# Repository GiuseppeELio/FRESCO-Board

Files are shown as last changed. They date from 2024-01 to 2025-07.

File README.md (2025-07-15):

#       PRC Measurement Station including TDrop and PCool
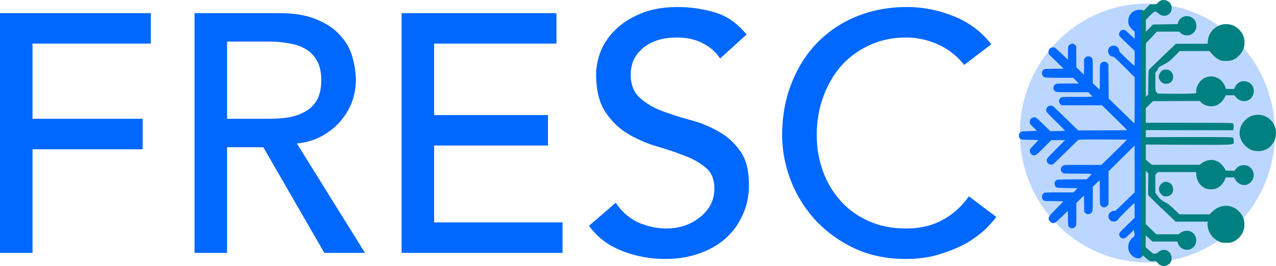
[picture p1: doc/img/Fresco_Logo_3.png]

## Introduction and scope 

The code reported in this repository are related to a data logger realization able to measure the temperature drop and the cooling power of "passive radiative cooling" samples. The device is covered by the OSHWA certificate and the GPL license with the UID IT0000015 and the details are available at the [following link](https://certification.oshwa.org/it000015.html) 
<p align="right">
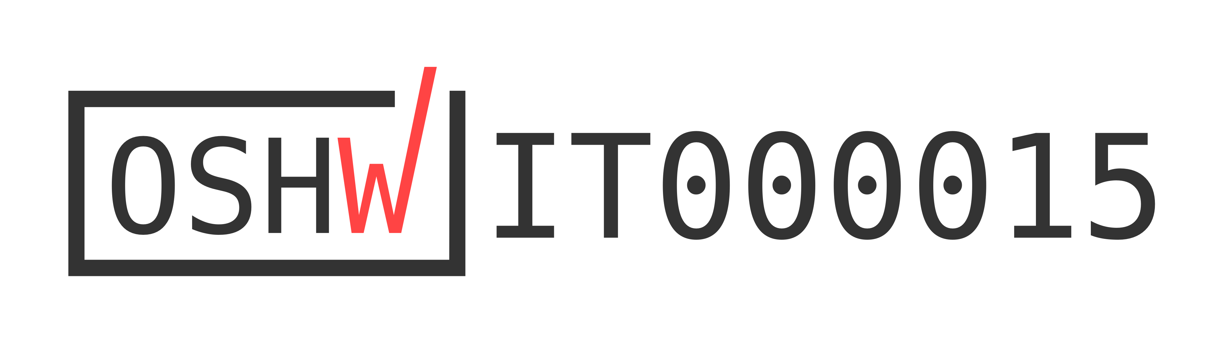
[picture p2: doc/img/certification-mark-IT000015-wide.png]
  
</p>

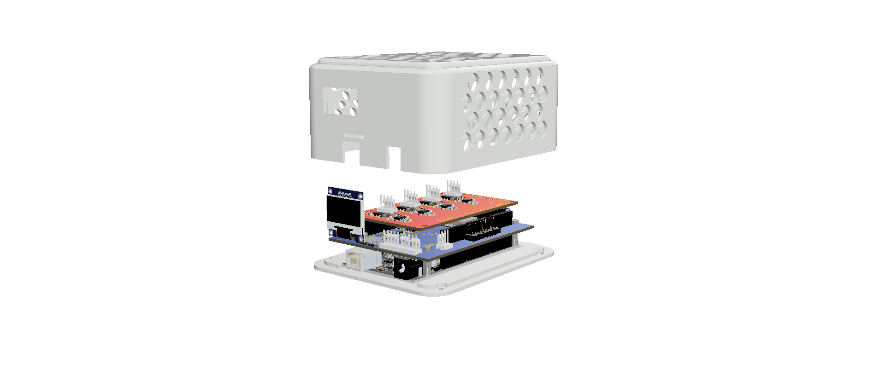
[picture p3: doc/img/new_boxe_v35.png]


The board as shown in the figure is composed by a main board, a TDrop shield that allows measuring the temperature for multiple samples, the solar irradiance, the sky temperature using an IR sensor, ambient temperature and relative humidity using a DHT22, store data on a onboard SD card. It is also equipped with a RTC clock for the correct time and a ESP8266-12F module for the WiFi connection and communication. The PCool shield is equipped with NTC to measure the sample temperature and a PID system to warm-up them to the setting point temperature that usually is the ambient temperature. 

The entire documentation will be soon available on the Zenodo repository at the following link [https://doi.org/10.5281/zenodo.13919077](https://doi.org/10.5281/zenodo.13919077)

Details about the device desgin, research and the results obtained with FRESCO are available on the following paper [https://www.cell.com/cell-reports-physical-science/fulltext/S2666-3864(25)00287-5]

You can refer or cite it using: 

Werlé, J., Concas, R., Pini, E., Wiersma, D. S., Pattelli, L., & Lio, G. E. (2025). Open-hardware platform for synchronous performance testing of multiple passive radiative cooling materials. Cell Reports Physical Science.

## Acknowledgements.

The inventors of FRESCO acknowledge the economic support offered by the CoolingPhotonics Company in the research project under techonoligcal transfer agreement named "FRESCO - Data Logger".  They also thanks the scientific  fruitful discussion offered in the framework of the PaRaMetric (EURAMET - European Partnership on Metrology), and the technical support offered by the joitlab - electronic workshop- of University of Florence and National Metrology Institute of Italy (INRIM). 

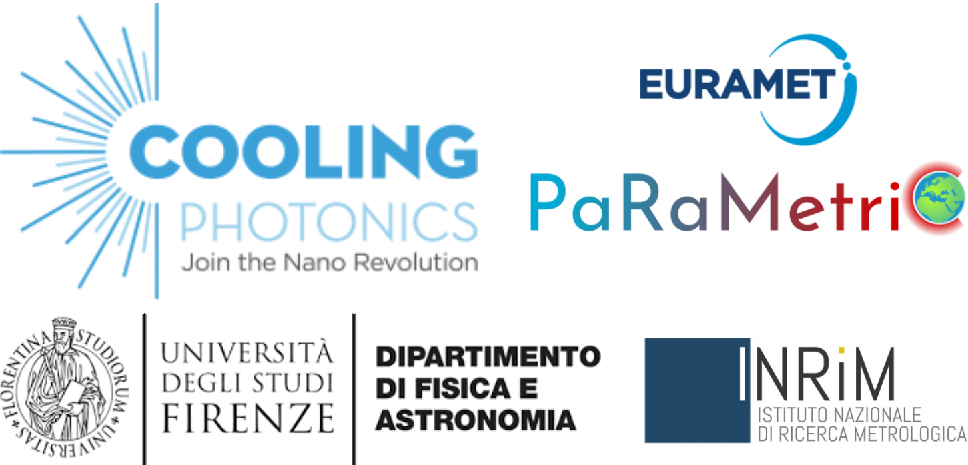
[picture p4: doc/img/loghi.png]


## A supporter is worth a thousand followers.

Dear reader, if you are interested in the development of FRESCO and its improvement with new features, please support our team by using the support button or by going directly to 
"Buy Me A Coffee" (https://buymeacoffee.com/gpplio93sx). We are actively working to do our best to achieve a reliable passive radiative cooling measurement apparatus. With your support we will move forward in developing new features, improve the web application experience and make it more essential for your experiments. You can support us directly buying coffees or with a membership. 

##       Software details

<p align="right">
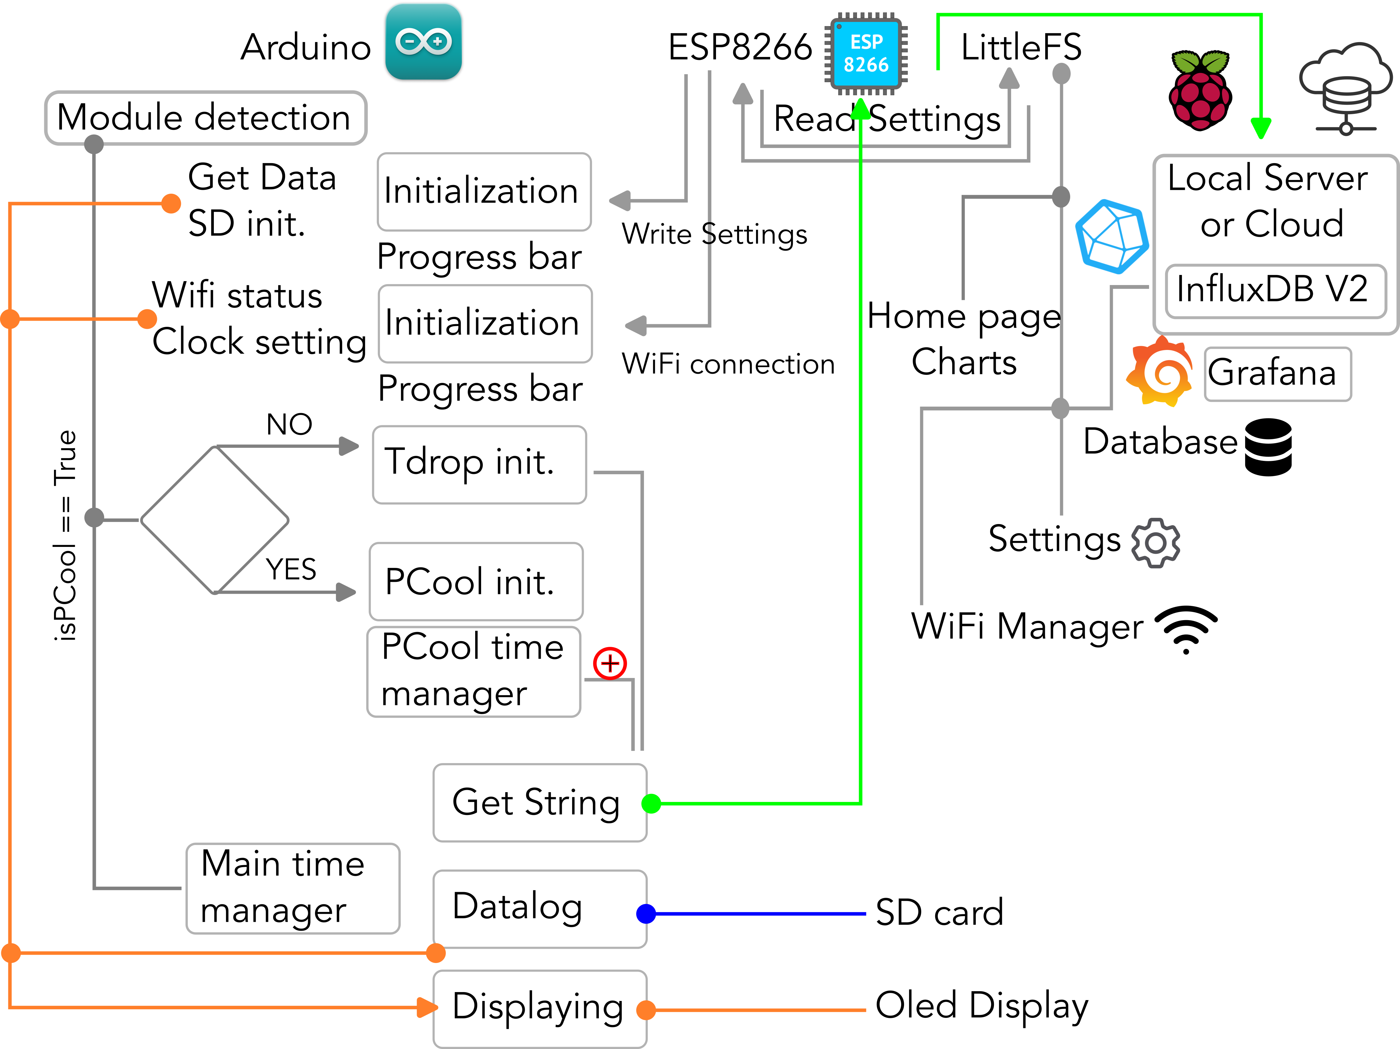
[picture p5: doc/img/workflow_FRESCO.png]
  
</p>

The schematic representation reports the workflow among Arduino, the ESP8266 for the WiFi communication, data exchange and remote storage using a local server (Raspberry) or cloud based on InfluxDB V2 and Grafana for the data visualization.

In order to use the choseen sensors that equip the TDrop shield such as: BH1750 (irradiance), Dallas DS18B20 (Temperature), DHT22 (temp and Humidity), DS3231 (clocker), and MLX90614 (IR temperature Ambient (near) and Sky (far))
it is necessary to install/ include the available [libraries](https://github.com/GiuseppeELio/FRESCO-Board/blob/main/libraries.zip).

## Temperature probes

In the following downloadable document [NTCs](https://github.com/GiuseppeELio/FRESCO-Board/blob/main/doc/Advised%20NTC%20thermocouples.pdf) you can find the B (K) constant values for the reccomended NTCs that have been tested. 

## ESP8266 WiFi connection and data transmissione. 

As reported in the pdf file ["FRESCO Board startup_Software"](https://github.com/GiuseppeELio/FRESCO-Board/blob/main/doc/FRESCO%20Board%20startup_Software.pdf) the FRESCO board is equipped with a WiFi network board to communicate and exchange information through a network and show the data directly on your device by a hot spot netwrok or connecting on the local IP of the selected WiFi. On the other hand, it allows sending the data on a remote server using Raspberry or a Linux PC/Server and then save the data on "InfluxDB V2" and display them on "Grafana" dashboard. 

## Python Temperature Drop and Cooling Power analysis 
Using the provided Jupyter Notebook [analysis.ipynb](https://github.com/GiuseppeELio/FRESCO-Board/blob/main/Scripts/analysis.ipynb) is it possible to display all the information collected using FRESCO and have an immediate look to the passive radiative cooling material features. The python script contains also a initial part that has been tought to merge the collected data stored in different subfolders, it means e.g merging the data in the folder year 2024 --> month 07 --Z from the day 8 to 17. An example is reported below. 

<p align="right">
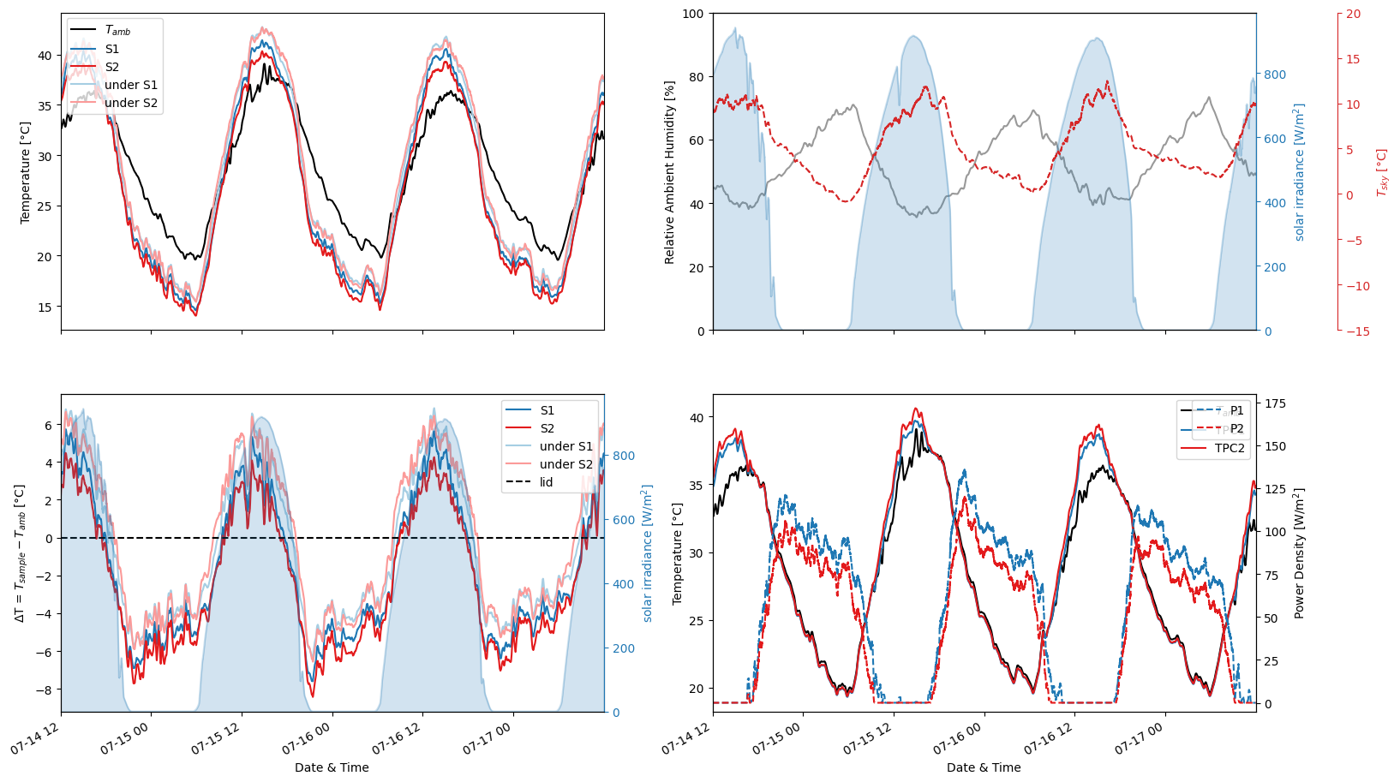
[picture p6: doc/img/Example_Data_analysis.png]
  
</p>

## Grafana Dashboard

Here it is reported an example of the full FRESCO dashboard realized using Grafana and it is displaying the temperature for each sensor (DHTs, NTCs, IR) the solar irradiance, the temperature drop in chart and gauges and also the cooling power is reported using charts (power and the setting point temperature) and gauges. You can find at the following link [FRESCO_DashBoard_Grafana.JSON](https://github.com/GiuseppeELio/FRESCO-Board/blob/main/doc/FRESCO_DashBoard_Grafana.JSON) the JSON file to make your dashboard as this one or to customize it.  

<p align="right">
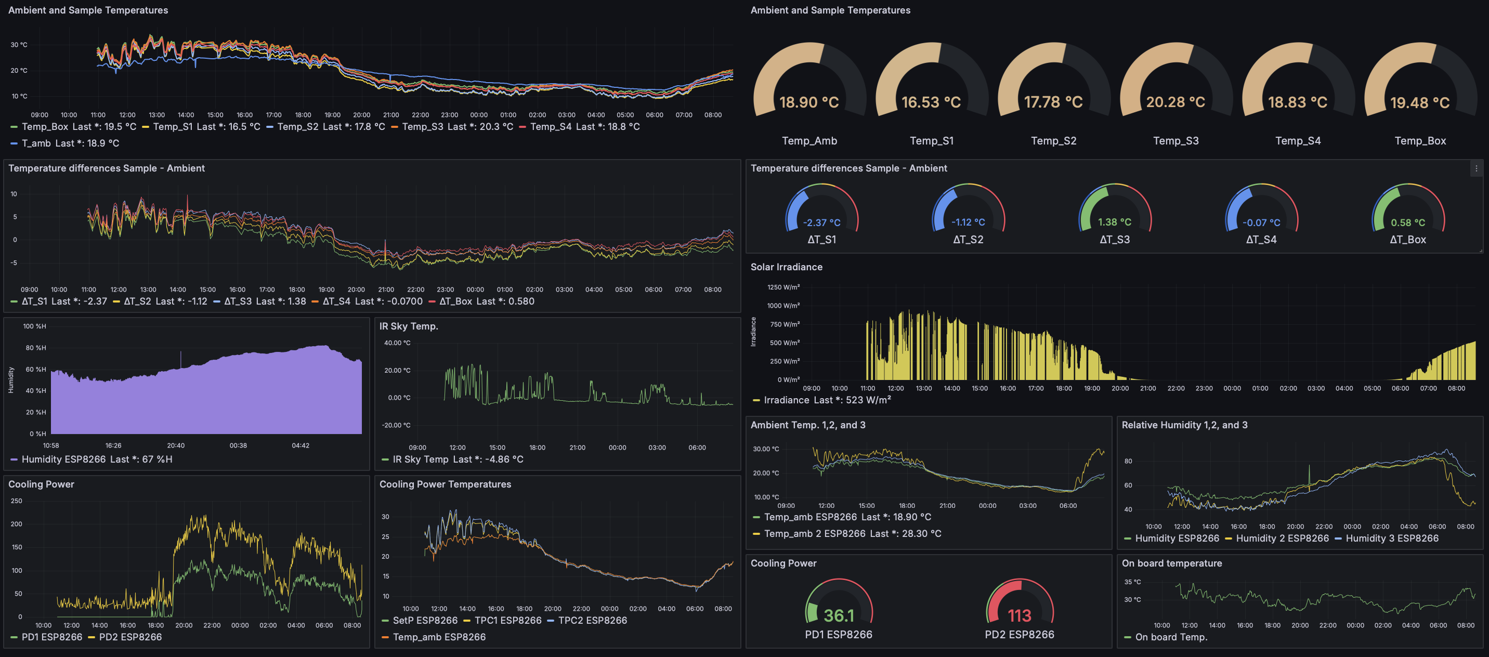
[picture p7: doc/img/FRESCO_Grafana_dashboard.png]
  
</p>

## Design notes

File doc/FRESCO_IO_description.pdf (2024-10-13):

## TDrop I/O pin description

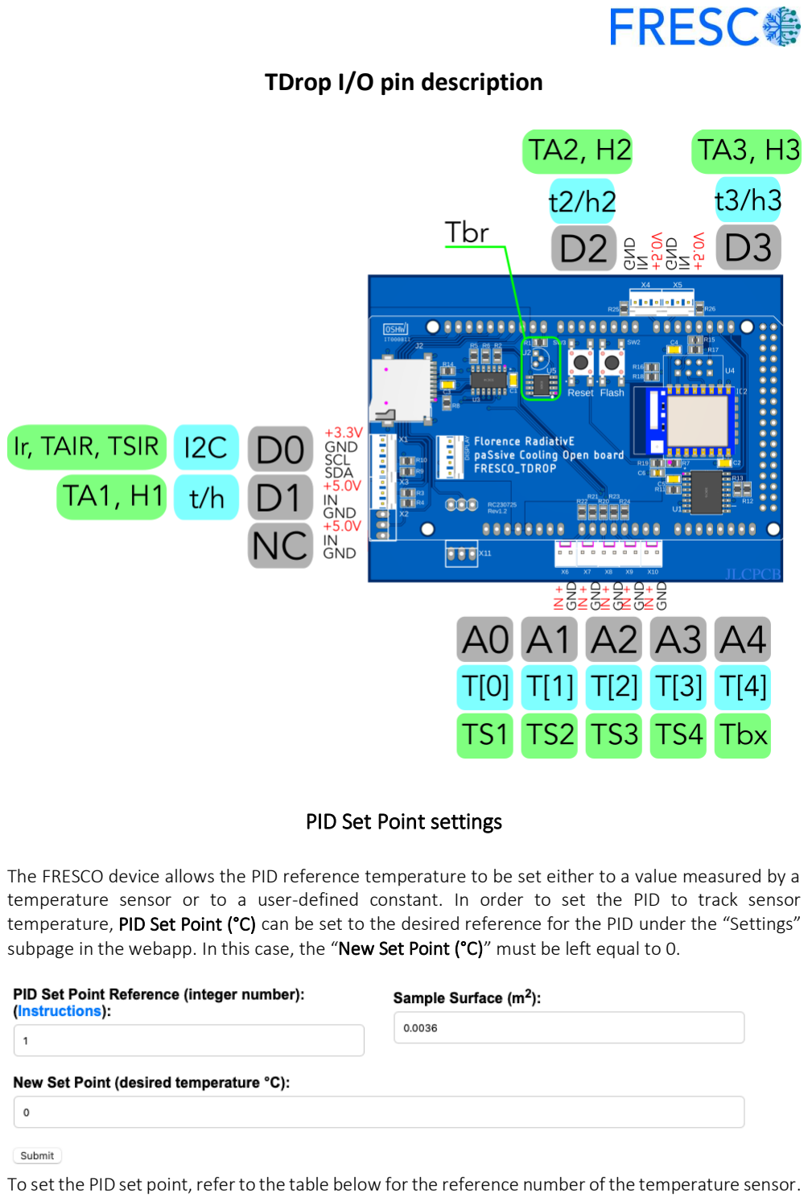
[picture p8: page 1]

PID Set Point settings

The FRESCO device allows the PID reference temperature to be set either to a value measured by a temperature sensor or to a user-defined constant. In order to set the PID to track sensor temperature, PID Set Point (°C) can be set to the desired reference for the PID under the “Settings” subpage in the webapp. In this case, the “New Set Point (°C)” must be left equal to 0.

To set the PID set point, refer to the table below for the reference number of the temperature sensor.

Reference numbers | Corresponding I/O sensor | Name on the saved file
0,1 | t | TA1
2 | t2 | TA2
3 | t3 | TA3
4 | T[0] | TS1
5 | T[1] | TS2
6 | T[2] | TS3
7 | T[4] | TS4
8 | T[5] | Tbx

The names on the cyan labels in the figure above correspond to their respective I/O sensors, and their values are stored on the SD card under the names indicated by the green labels.
If the value entered in the PID Set Point (°C) does not match any predefined options, the set point will default to TA1.

Alternatively, the PID can be set to track a fixed user-defined temperature by setting the PID Set Point (°C) equal to 10 and then using New Set Point (°C) to indicate a temperature value between 0 °C and 60 °C (e.g., 32.5°C). As in the previous case, the PID Set Point (°C) will default to TA1 for invalid input.

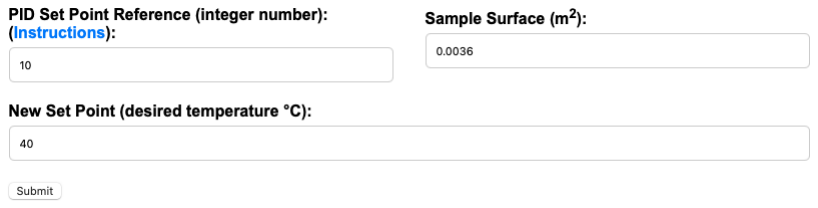
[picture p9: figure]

After pressing “Submit” the ESP will restart, so if you have to operate also on other settings like the WiFi or the Database you can wait the ESP restart and do it, but the measurements will be not aligned. While if you already did all the needed things, you can turn off the power supply of the FRESCO and turn on again to get a well alignment among Tdrop, PCool and the ESP microcontroller.

In the next page you will find the I/O ports referred to the PCool board and all useful reference already listed in the table of the previous section.

## PCool I/O pin description

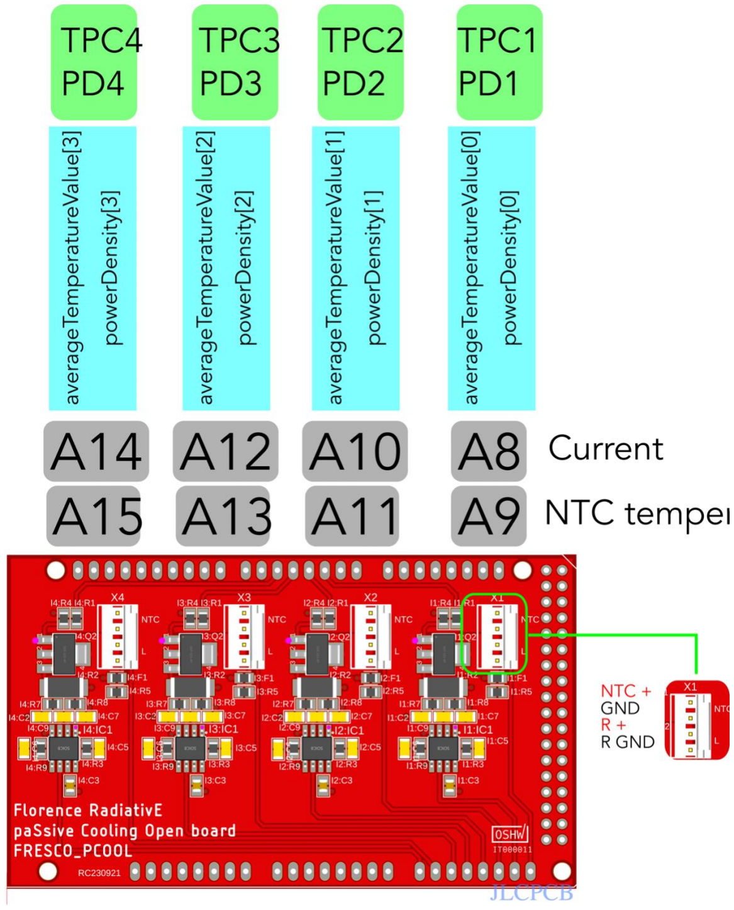
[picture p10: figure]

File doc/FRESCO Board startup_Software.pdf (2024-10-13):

Manual V2 Edited by Giuseppe E. Lio, PhD

## FRESCO Board startup

Software

### Index

## Integrated Web-App

After power supplying the FRESCO board, using a smartphone or a laptop with a WiFi connection find the WiFi network with the SSID named
“FRESCO-board” | and | use | the | password
“123456789”. Once the device is connected navigate using your browser to the “local IP” displayed on the oled screen, commonly it is 192.168.4.1. You will directly be redirected to the web app page and the following screenshot will be displayed.

The web app will directly display the collected data in the two double Y axis plots. Clicking on the labels you can choose to hide or not the selected measurements.

Using the three buttons placed at the top is possible to manage the WiFi connection ( ) over

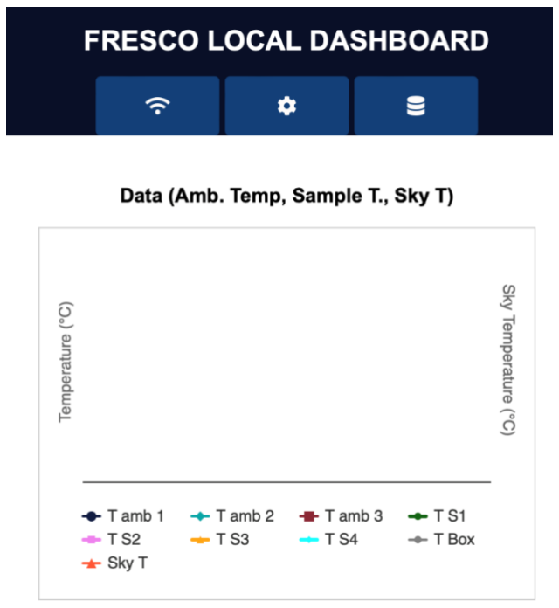
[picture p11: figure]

an external network, the ESP settings ( ) and to manage the database connection ( ).

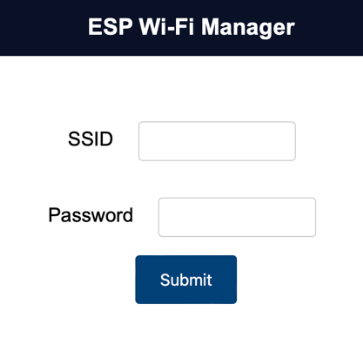
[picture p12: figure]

## WiFi manager ( ) and connection to external network

The panel reported on the left, after clicking on the dedicated icon, allows including two entries for the external network connection.
In the SSID field it will be indicated the name of the network selected for the connection and in the Password field the associated field.

Once these values will be submitted the ESP will restart and after a while it is important to turned off and turned on again the entire FRESCO board, it is important to get a well alignment between the read and transferred data.

After that, the ESP will be connected to the external network, the main web page will display the IP where it is connected on the external network and the local IP as depicted in the Figure on the left.

## Usage of the Database ( )

Once the button is clicked you will redirected to the following page and you can set the main input entries for InfluxDB V2. The next lines report the list of the entries that have to be written in the web app.

INFLUX_URL
INFLUXDB_ORG (organization ID)
INFLUXDB_BUCKET (the database name)
INFLUX_TOKEN (the password to connect the device to the database in a unique way.)

The following parameters can be collected by using the InfluxDB cloud or V2 installed on a local server. The next two sections will be devoted to explain step by step how to connect and setup the database and the dashboard to see the output data.

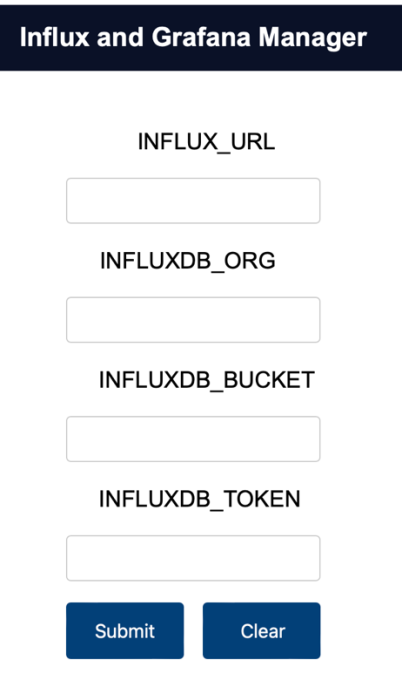
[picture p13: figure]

Once these values will be submitted the ESP will restart and after a while it is important to turned off and turned on again the entire FRESCO board, it is important to get a well alignment between the read and transferred data.

## Settings ( )

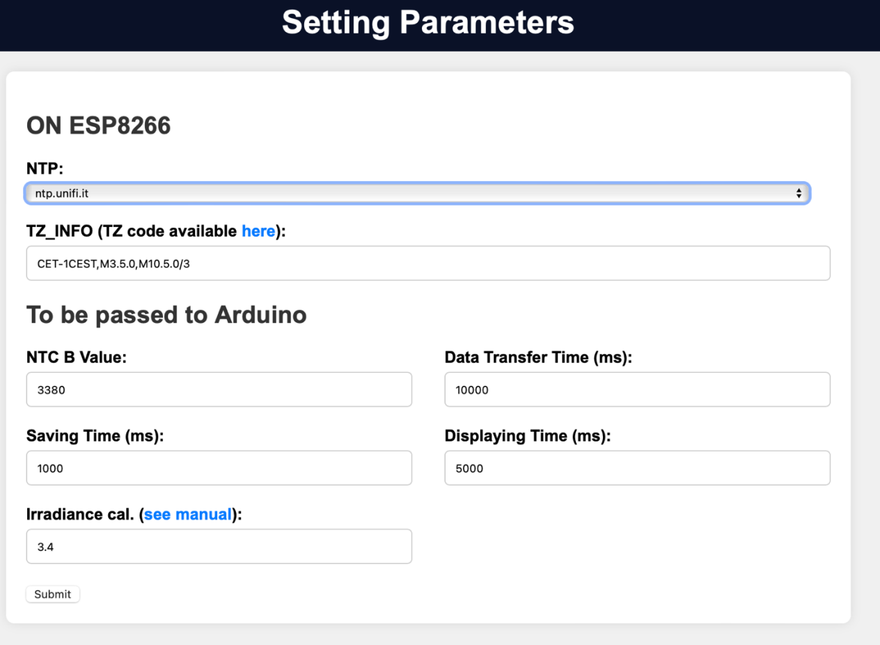
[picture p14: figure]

The setting web app page allows the user to manage the following entries:

Once the FRESCO device is connected to the WiFi, the NTP is needed to setup correctly the network time protocol useful for the certification to access and send data to InfluxDB (local and cloud version) but it is also important to align the RTC time on the device. According to the network should be necessary to change the NPT and it is possible thanks to the drop-down menu. The user can select the suitable NTP address from the list.

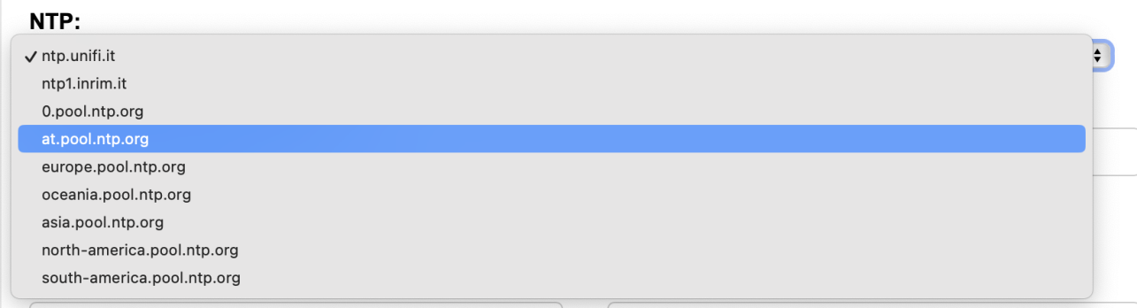
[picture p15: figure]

After the NTP selection it is also important for a correct time alignment to select the time zone (TZ_Info) and it is possible directly writing the unique code associated to the different TZ. The list of the codes is available at the following link or clicking in the webapp link. https://github.com/nayarsystems/posix_tz_db/blob/master/zones.csv
for example:
Europe/Amsterdam CET-1CEST,M3.5.0,M10.5.0/3

Indicates the Central European Summer Time (CEST) that take in account the winter and summer time shift, the Standard and Day Saving Time (DST) and automatically it allows aligning the RTC time avoiding any kind of delay.

In the section “To be passed to Arduino” is is possible to set other entries such as:
- The Beta (also called K const) value related to the used NTC (pay attention to use 10k Ω NTCs).
- “Data Transfer Time” The time to transfer the data over the ESP and the webapp or the Database.
- “Saving Time”: The time to save the data on the SD card (local database).
- “Displaying Time”: The time to display the information over the Oled display.
- “Irradiance cal.”: this value is used to calibrate the BH1750 with the mounted “dome”, if it results not well aligned with some weather station data can be used to re-align it.

Please pay attention that all the time have to be integer and are expressed in milli seconds, hence 1 second have to be written as 1000 ms.

FRESCO is now able to automatically detect if another shield such as PCool is mounted, in this case the settings, but also the main page, provide to the user other entries (or charts) and it is possible to set some parameters related to the PID.

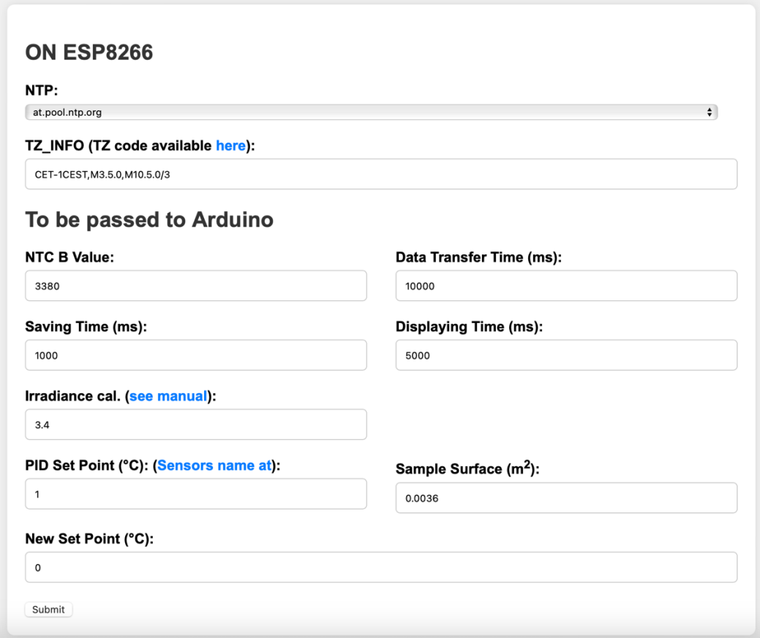
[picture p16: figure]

In this case it is possible to set the PID Set Point, the Sample Surface used as substrate and to evaluate the cooling power density and in case a New Set Point (°C) to directly set the desired temperature to drive the PID. All the details about it’s working principle are available at the following link
https://github.com/GiuseppeELio/FRESCO-Board/blob/main/doc/FRESCO_IO_descript.pdf

## Cloud InfluxDb and Grafana configuration

First of all to use the InfluxDB cloud it is necessary to go at the following link https://cloud2.influxdata.com/signup
and register an account, once you are logged in you will find the following interface

Then you have to configure the database to work accordingly to a ESP8266 wifi and Arduino board,

to to that go on sources ( ) in the left menu and you will be directly moved on the following page

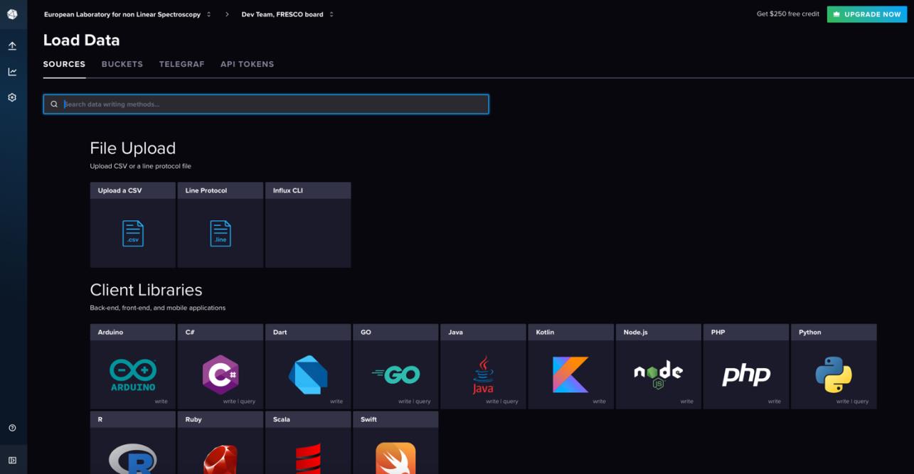
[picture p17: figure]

There you have to select “Arduino”, then it will start a guided procedure and make sure to select ESP8266 as reported in the next screenshot.

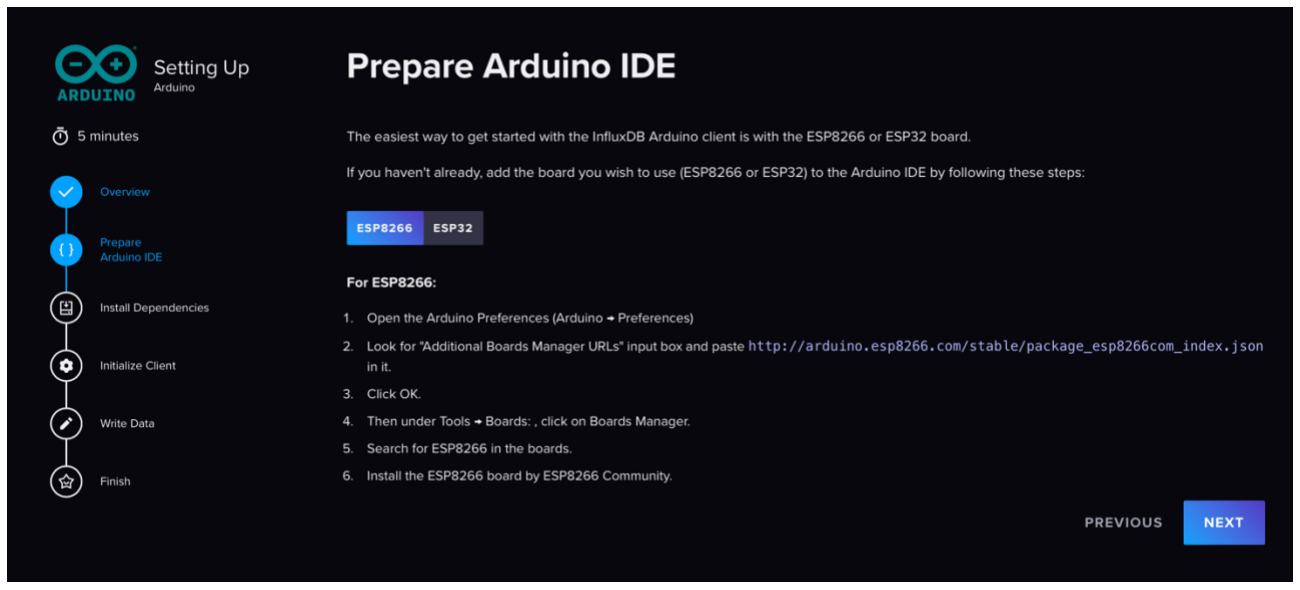
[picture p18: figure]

Then in “initialized client” you will define the name of your Bucket so you can left ESP8266 or you can change it as you prefer. Then, scrolling down you will arrive to the main important part, where it is displayed, and please remember that you will see them just now (if you lost the following credentials you have to do all the things again from a scratch.)

The highlighted parts are the entries required in the databse web app manager. Conclude the guided procedure until “Finish”. Once it has been created is time to include the parameters indicated before in the InfluxDB manager as following

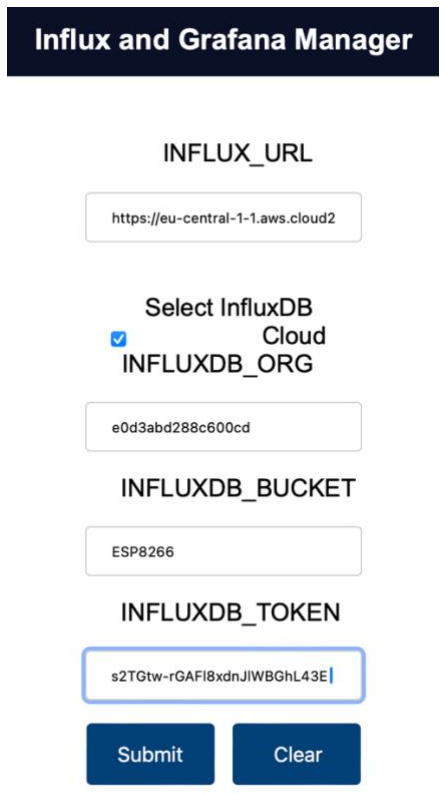
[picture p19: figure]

Now it is necessary to use the InfluxDb webpage on the “Data Explorer” to see if the FRESCO board is transmitting the data, if it is yes on the left columns selecting the Bucket it will appear the field “Measurements”, this is a proper name given to the data collection directly by the FRESCO device.

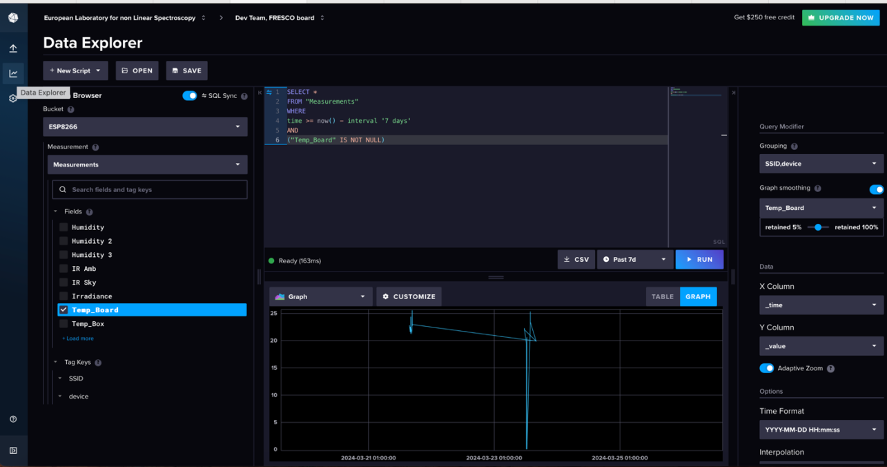
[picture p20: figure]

Once the label “Measurements” has been selected all the contained data will be displayed in the menu placed below of it. Selecting for example Temp_Board and the time interval in the center, under the code generator, and then Run a table of data or a graph will be plotted. The generated SQL code will be important for the next steps.

Here it is a simple SQL example to recall the data that we would like to visualize

SELECT time, | "Temp_Board"
FROM "Measurements"
WHERE time >= now() - interval | '15 minutes'
AND ("Temp_Board" IS NOT NULL)

The highlighted parts are referred to the variable that we would like to see and the interval time. It is important to know that more than one variable for instance can be shown, it is enough to write for example

SELECT time, "Temp_Board", “Temp_S1”, “Temp_S2”

And to change the time interval can be minutes, hours or days. If you are referring to a single minute, 1 hour or 1 day use the single form of such word.

GRAFANA
Now is time to use the stetted-up database and SQL codes for the Grafana Dashboard a simple and efficient way to visualize the collected data in real-time and whenever you want.
Start going to the following web page and create your GRAFANA Free account. (https://grafana.com/products/cloud/?src=ggl-s&mdm=cpc&camp=b-grafana-exac-emea&cnt=118483912276&trm=grafana&device=c&gad_source=1) Then you can go directly to “My account”, and click on “Launch” your Grafana

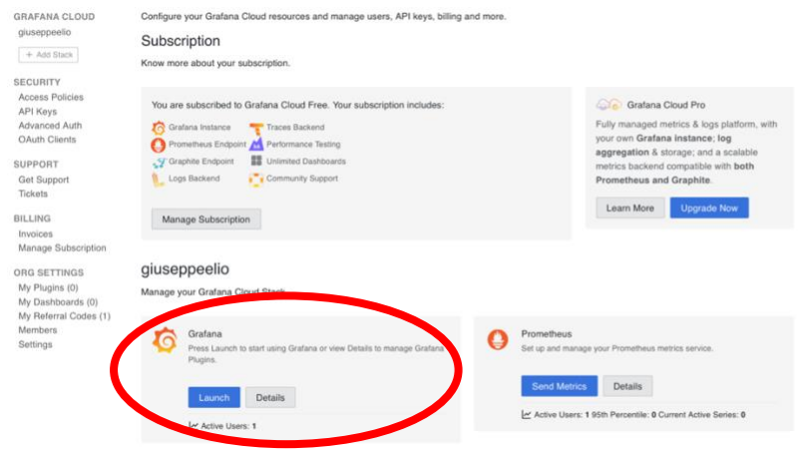
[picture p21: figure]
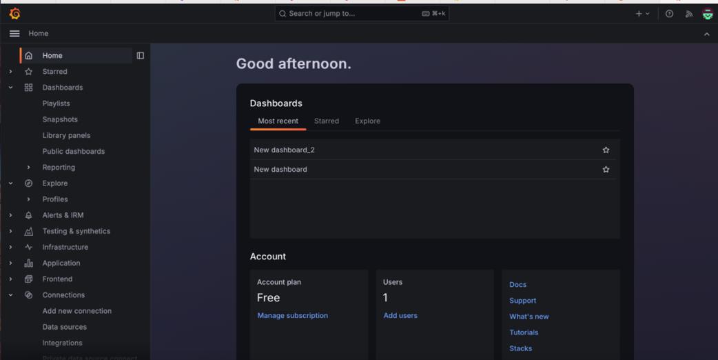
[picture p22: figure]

And you will reach the following webpage

Here it is important to go on the left menu and scroll down until you are at the item “Connections” and then “Data sources”. Once you are here you have to press “+ add data source”, in the menu that will be opened select “infuxDB”

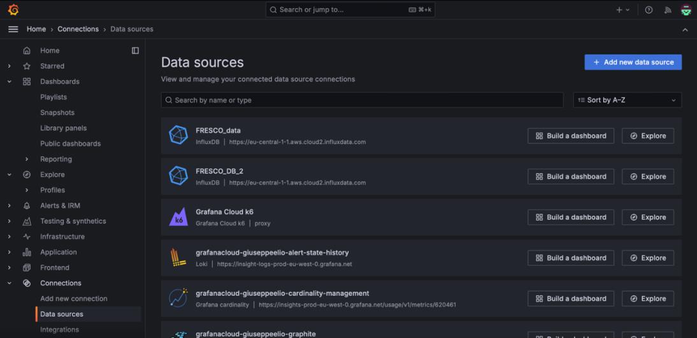
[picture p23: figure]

Following the next steps you will be able to connect Grafana to the database.
As reported in the following screenshot you can chose the name of the of the data source, and the Query language, be careful to select SQL. Then in the HTTP you have to indicate the InfluxDb Cloud web address that is something like “https://eu-central-1-1.aws.cloud2.influxdata.com”

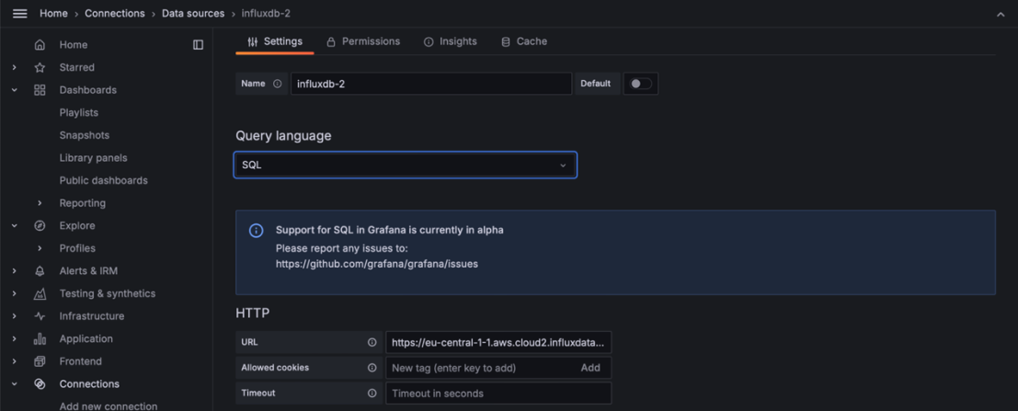
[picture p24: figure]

Once all these field are filled the next one, available scrolling the page, are:
Toggle on the use of Basic Authentication and in the related field use as User and Password the same credentials that you use for the InfluxDB Cloud.

In the next two field it is necessary to indicate the Bucket and the Token again and then press “Save & test”.

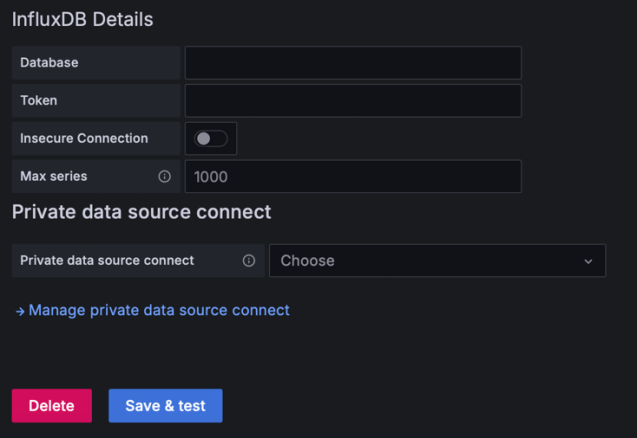
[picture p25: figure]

If all the indicated inputs are correct you will display the following banner.

So now is time to go back to the Grafana Dashboard creation, in the “Dashboard” section press on “New”>”New Dashboard”

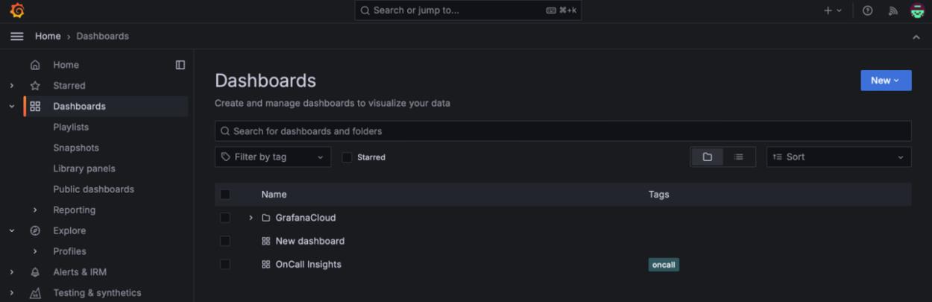
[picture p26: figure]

And you will display the following screen view and here you have to press on “+ Add visualization” and select the “Data source” and select the one created in the previous steps.

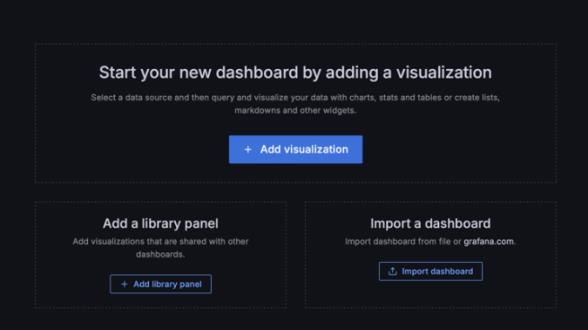
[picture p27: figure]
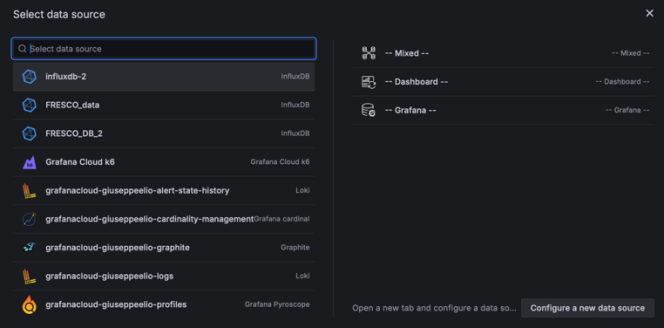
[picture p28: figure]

Then you will be redirected to the following interface and here you have to select in the Query A the voice related to “code”, now, here we can use the SQL code to see the data

For example, including the following SQL code:
SELECT time, "Temp_Board"
FROM "Measurements"
WHERE time >= now() - interval '7 days'
AND ("Temp_Board" IS NOT NULL)

And pressing “Run query” it will display the collected data in the last 7 days, of course you can modify the time as you prefer. In the same chart is possible to add more Query just going on the bottom part of the chart and pressin “+ Add query”, then repeating the same procedure is possible to add another curve plotted in the same chart. In any case as already discussed before is

possible to add multiple items modifying the script as follow e.g SELECT time, "Temp_Board", “Temp_S1”, “Temp_S2”. Different queries are useful for double Y axis or different way to visualize the data.

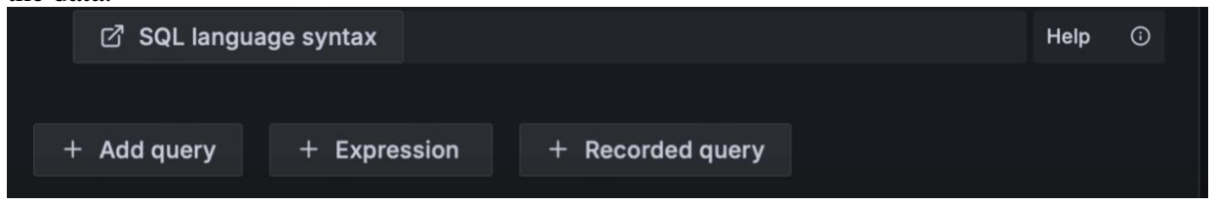
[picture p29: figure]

Once these values will be submitted the ESP will restart and after a while it is important to turned off and turned on again the entire FRESCO board, it is important to get a well alignment between the read and transferred data.

Now using the menu on the right side you can tailor the plots as you want, you can add more items in the same chart, change color lines, change the kind of plot from Time series, to histograms or gauges or what the user prefer. In any case Grafana is very flexible for all the usage and to be customized according to the user requirements.

The menu reported on the right

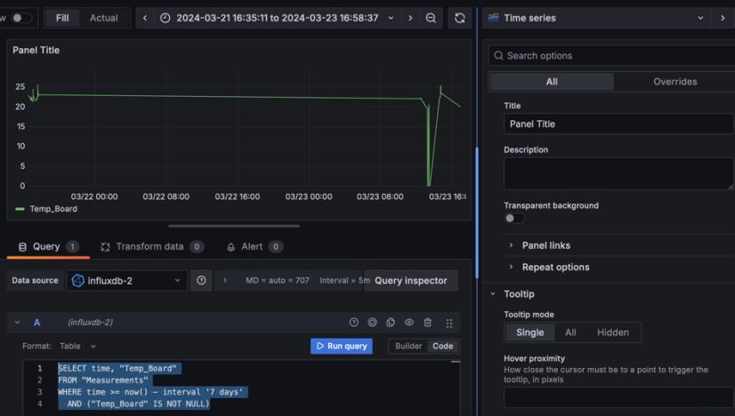
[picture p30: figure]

side, accessible using the right side column in the previous interface, allows selecting different kind of charts or plots. It is possible to select the Time series, commonly used for data that change during the time, but also bar chart, statistical one that reports a banner with the last value measured, gauge meters, table to list the values, Pie chart or histograms and others.

It is also important that a dashboard can be easily imported using the related Json structure file. This allows to duplicate or manage an already existing Dashboard in Grafana and make it suitable for the selected purposes.

## Local InfluxDb and Grafana configuration

This section will be devoted on the procedure to set up a local server able to host a personal InfluxDb and Grafana. It will be expanded in the next time with all the advice related to prepare a Raspberry Pi (3 or 4 all models).

About the procedure to be followed to install InfuxDB V2 on a Raspberry or a Ubuntu (Linux) PC
see | the | following | guide
https://docs.influxdata.com/influxdb/v2/install/
As reported on this web page it is recommended to install a Ubuntu supported version on the
RaspBerry | | | Pi

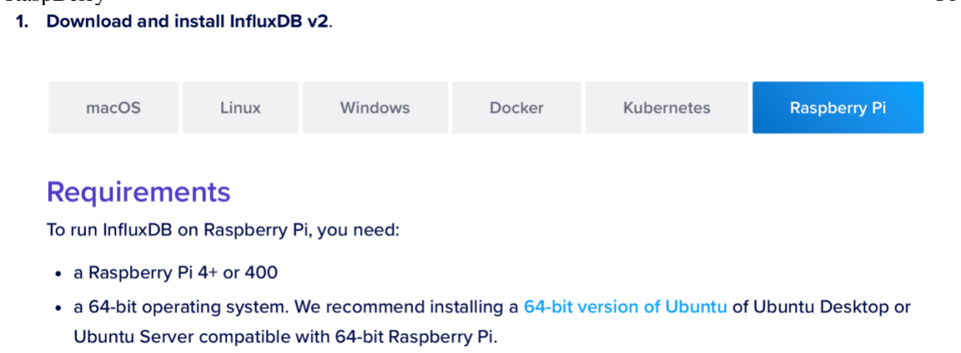
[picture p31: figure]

Details about this procedure are reported here https://ubuntu.com/download/raspberry-pi you need to download the Raspberry Pi image https://www.raspberrypi.com/software/ and install the Ubuntu stable version for IOT for 64 bit processor.


Once | you | have | selected | the | RaspBerry model that you posses

you can choose the Operative system; your; Raspberry Pi.

| | | | | From this interface you have to select Raspberry Pi OS (Other), and you will go to the following page and select Raspberry Pi Os (Legacy 64- Bit) Lite (Bullseye distribution).

Finally, you can select the SD card used to startup and install the OS in

Once this operation have been done, you can perform the procedure to set a static IP on your server as reported in the following guide https://phoenixnap.com/kb/raspberry-pi-static-ip it works for RaspianOS but also for other the Linux distributions.

If you posses a Static IP follow this guide to set up the static IP on your Raspberry https://phoenixnap.com/kb/raspberry-pi-static-ip

At this point the important poit is the use of the following command line
sudo nano /etc/dhcpcd.conf

It allows opening the dhcpcd configuration file and set the suitable values at the following lines:
interface [interface-name]
static ip_address=[ip-address]/[cidr-suffix]
static routers=[router-ip-address]
static domain_name_servers=[dns-address]
pay attention about the cidr-suffix, it depends on the subnet mask of your network, you can find the appropriate values at the following website. (https://www.freecodecamp.org/news/subnet-cheat-sheet-24-subnet-mask-30-26-27-29-and-other-ip-address-cidr-network-references/) The common value for cidr-suffix is 24.

be careful also to modify the item that are out of comment, in the conf file the commented lines are identified by #.

A possible example is where, of course, X,A,B,C,D,E,F are numbers
interface eth0
static ip_address=XXX.XXX.XXX.XXX/24
static routers=XXX.XXX.AAA.BBB
static domain_name_servers=XXX.XXX.CCC.DDD., XXX.XXX.EEE.FFF

Then, save the file and exit (normally is required to follow the instructions reported below in the console/ terminal).

Finally, reboot Raspberry Pi by typing:
sudo shutdown -r now

InfluxDB V2 installation

After these initial steps to prepare the Raspberry Pi to host the InfluxDB V2 you can follow these
simple | steps | to | install | it

In the terminal – console use the following commands:
curl -O https://dl.influxdata.com/influxdb/releases/influxdb2_2.7.5-1_arm64.deb sudo dpkg -i influxdb2_2.7.5-1_arm64.deb

Then start the service using the command line
sudo service influxdb start

and check the status using
sudo service influxdb status

If successful, the output is the following:
- influxdb.service - InfluxDB is an open-source, distributed, time series database Loaded: loaded (/lib/systemd/system/influxdb.service; enabled; vendor preset: enable>
Active: active (running)

If successful, you can view the InfluxDB UI at http://localhost:8086, in case you use a static IP you can view it at http://IP:8086 or http://domain.something.com:8086

Arrived to this point, the procedure to setup your influxDB V2 local version is the same of the Cloud one as already described in the previous section. So also in local is necessary to generate the Token, the Bucket and to get the ORG ID code. The difference is in the URL that now is http://localhost:8086, in case you use a static IP you can view it at http://IP:8086 or http://domain.something.com:8086

Grafana

To install Grafana open the terminal/ console and insert the following command:
Install the prerequisite packages:
sudo apt-get install -y apt-transport-https software-properties-common wget

Then, import the GPG key
sudo mkdir -p /etc/apt/keyrings/
wget | -q | -O | - | https://apt.grafana.com/gpg.key | | | gpg | --dearmor | | | sudo | tee
/etc/apt/keyrings/grafana.gpg > /dev/null

To add a repository for stable releases, run the following command:
echo | "deb | [signed-by=/etc/apt/keyrings/grafana.gpg] | https://apt.grafana.com
stable main" | sudo tee -a /etc/apt/sources.list.d/grafana.list

To add a repository for beta releases, run the following command:
echo "deb [signed-by=/etc/apt/keyrings/grafana.gpg] https://apt.grafana.com beta
main" | sudo tee -a /etc/apt/sources.list.d/grafana.list

Run the following command to update the list of available packages:

# Updates the list of available packages

sudo apt-get update

To install Grafana OSS, run the following command:
# Installs the latest OSS release:

sudo apt-get install grafana

Reboot Raspberry
sudo reboot
or
sudo shutdown -r

Start the Grafana server

Follow this procedure to start the Grafana server with systemd
Complete the following steps to start the Grafana server using systemd and verify that it is running.

To start the service, run the following commands:
sudo systemctl daemon-reload
sudo systemctl start grafana-server
sudo systemctl status grafana-server

To verify that the service is running, run the following command:
sudo systemctl status grafana-server

On the other hand, you can Start the Grafana server using init.d
Complete the following steps to start the Grafana server using init.d and verify that it is running:
sudo service grafana-server start
sudo service grafana-server status

To verify that the service is running, run the following command:
sudo service grafana-server status

[Optional procedure]
On the other hand you can also configure the Grafana server to start at boot using init.d To configure the Grafana server to start at boot, run the following command:
sudo update-rc.d grafana-server defaults

Restart the Grafana server using init.d
To restart the Grafana server, run the following commands:
sudo service grafana-server restart

If successful, you can view the InfluxDB UI at http://localhost:3000, in case you use a static IP you can view it at http://IP:3000 or http://domain.something.com:3000

The port 3000 allows acceding to the Grafana interface, register your account, please initially it has the username to access “admin” and the password “admin”, this password will be required to be changed immediately after the first access.

Configuration of Influx Data Source on Grafana

Finally, the local configuration of Grafana is quite similar to the one reported in the previous section for Grafana Cloud, the exceptions are the following:
1) in the “Data source” connection the Data Base INFLUX URL is the one
used for the local InfluxDB V2.
2) The Data source connection on local Grafana uses the FLUX language instead of the SQL one, so follow the following steps to set it up.

Now you can go on the left menu and scroll down until you are at the item “Connections” and then “Data sources”. Once you are here you have to press “+ add Data sources”, in the menu that will be opened select “influxDB”

Once the InfluxDB Data source has been addend, the following window will appear
Be sure to select as Query language Flux


The other parameters and setting remains equal to the one used in the Cloud version, except for the fact that now is required the Organization name, a parameter that you have already setted when you start up the local InfluxDB.

To retrieve the Organization name you can go on InfluxDB page and find it under the account name.

Once everything has been done, you can move back to configure the Dashboard on Grafana, in this case the Query language to be included will have the following form

from(bucket: "ESP8266")
|> range(start: v.timeRangeStart, stop: v.timeRangeStop)
|> filter(fn: (r) => r["_measurement"] == "Measurements")
|> filter(fn: (r) => r["_field"] == "Temp_amb" or r["_field"] == "Humidity") |> aggregateWindow(every: v.windowPeriod, fn: mean, createEmpty: false)
|> yield(name: "mean")

And it is retrieved by InfluxDB again using the Data Explorer section.

The dashboard and its Json code are available at the following link. (https://github.com/GiuseppeELio/FRESCO-Board/blob/main/doc/FRESCO_DashBoard_Grafana.JSON)

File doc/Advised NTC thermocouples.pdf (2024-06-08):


Tested and Advised NTC thermocouples

Name | Resistance at 25°C | B or K value
NTCLE350E4 | 10 kΩ | 3435

Link to buy (https://www.mouser.it/ProductDetail/594-NTCLE350E4502FLB)

Name | Resistance at 25°C | B or K value
103JT-025 | 10 kΩ | 3435

Link to buy (https://www.mouser.it/ProductDetail/954-103JT-025)

Name | Resistance at 25°C | B or K value
CTTS-203856-S02 | 10 kΩ | 3936

Link to buy (https://www.mouser.it/ProductDetail/527-CTTS-203856-S02)


Name | Resistance at 25°C | B or K value
NXFT15XH103FA2B100 | 10 kΩ | 3380

Link to buy (https://www.mouser.it/ProductDetail/Murata-Electronics/NXFT15XH103FA2B100?qs=MY6wChARw2w18C%2F%2FDH%252ByIQ%3D%3D)

Name | Resistance at 25°C | B or K value
10K MF52B | 10 kΩ | 3435

Link to buy (https://www.amazon.it/【Primavera-Vendita-Regalo】Sensore-temperatura-termistore/dp/B08HRFM2SP?__mk_it_IT=ÅMÅŽÕÑ&sp_csd=d2lkZ2V0TmFtZT1zcF9hdGY)

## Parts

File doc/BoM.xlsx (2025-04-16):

TDrop
Comment | Designator | Footprint | JLCPCB Part # | Quantity | Price Ex Vat
3.3kΩ | R2,R5,R6,R14 | RC0805JR-073K3L | C114222 | 4 | 0.01€
10nF | C6 | 0805B103K101NT | C128805 | 1 | 0.02€
SN74LVC125AD | U3 | SN74LVC125AD | C7661 | 1 | 0.20€
connector | DISPLAY,X1 | 640456-4 | C86504 | 2 | 0.23€
10kΩ | R7,R8,R11,R20,R21,R22,R23,R24 | RC0805JR-0710KL | C100047 | 8 | 0.02€
SD | J2 | TF-CARDH1.8SY | C7529391 | 1 | 0.05€
DS18B20Z | U5 | DS18B20Z+T&R | C97190 | 1 | 1.44€
DS3231S | U1 | DS3231SN#T&R | C9866 | 1 | 2.93€
connector | X3,X4,X5 | 640456-3 | C86503 | 3 | 0.30€
100Ω | R18,R19 | RC0805FR-07100RL | C105577 | 2 | 0.04€
CR2032-SMD | B1 | MY-2032-05-R | C964830 | 1 | 0.14€
100nF | C1,C2,C3,C4,C5 | FM31X104K101ECG | C525187 | 5 | 0.07€
ESP-07 | IC2 | ESP-07 | C82894 | 1 | 2.75€
C132131 | JP7 | DS1023-2*18SF11 | C132131 | 1 | 0.27€
switch | SW2,SW3 | TL3301NF160QG/P010515 | C273527 | 2 | 0.58€
Connector | JP1,JP2,JP3,JP4,JP5 | 2.54-1*8P | C27438 | 5 | 0.33€
0Ω | R15 | QR0603J0R00P05Z | C176152 | 1 | 0.06€
4.7kΩ | R1,R3,R4,R9,R10,R12,R13,R16,R25,R26 | ERJ6ENF4701V | C192064 | 10 | 0.07€
33kΩ | R17 | RMCF0805JT33K0 | C237765 | 1 | 0.18€
PCB manufacturing |  |  |  | 1 | 2.00€
PCB Assembly considering Extended components |  |  |  | 1 | 11.31€
 |  |  |  | Total TDrop | 22.99€
Pcool
Comment | Designator | Footprint | JLCPCB Part # | Quantity | Price Ex Vat
Connector | X1,X2,X3,X4 | 640456 | C86504 | 4 | 0.43€
10kΩ | I1:R5,I2:R5,I3:R5,I4:R5,I1:R7,I1:R8,I2:R7,I2:R8,I3:R7,I3:R8,I4:R7,I4:R8,I1:R5,I2:R5,I3:R5,I4:R5,I1:R7,I1:R8,I2:R7,I2:R8,I3:R7,I3:R8,I4:R7,I4:R8 | RC0805JR-0710KL | C100047 | 16 | 0.03€
100nF | I1:C2,I1:C5,I1:C6,I1:C7,I1:C9,I2:C2,I2:C5,I2:C6,I2:C7,I2:C9,I3:C2,I3:C5,I3:C6,I3:C7,I3:C9,I4:C2,I4:C5,I4:C6,I4:C7,I4:C9 | FM31X104K101ECG | C525187 | 16 | 0.22€
100kΩ | I1:R4,I2:R4,I3:R4,I4:R4 | RC0805FR-07100KL | C96346 | 4 | 0.01€
1Ω | I1:R2,I2:R2,I3:R2,I4:R2 | HoLRT2512-2W-1R-1% | C5127856 | 4 | 0.34€
AD820 | I1:IC1,I2:IC1,I3:IC1,I4:IC1 | AD820ARZ | C578639 | 4 | 18.42€
IRLL014NTRPBF | I1:Q2,I2:Q2,I3:Q2,I4:Q2 | IRLL014NTRPBF | C74066 | 4 | 1.00€
FERRITE_BEAD | I1:F1,I2:F1,I3:F1,I4:F1 | FBMJ2125HS250NT | C92883 | 4 | 0.21€
100nF | I1:C3,I2:C3,I3:C3,I4:C3 | C0805C104M5RAC7800 | C519981 | 4 | 0.15€
390kΩ | I1:R3,I1:R9,I2:R3,I2:R9,I3:R3,I3:R9,I4:R3,I4:R9 | RC0805JR-07390KL | C137442 | 8 | 0.04€
100Ω | I1:R1,I2:R1,I3:R1,I4:R1 | RC0805FR-07100RL | C105577 | 4 | 0.06€
PCB manufacturing |  |  |  | 1 | 2.00€
PCB Assembly considering Extended components |  |  |  | 1 | 11.31€
 |  |  |  | Total Pcool | 34.22€
IR sensor and Light sensor
Comment | Designator | Footprint | JLCPCB Part # | Quantity | Price Ex Vat
IR | IC1 | MLX90614ESF-BAA-000-TU | C490604 | 1 | 5.97
100nF | C1 | FM31X104K101ECG | C525187 | 1 | 0.03
Connector | X1 | 640456 | C86504 | 1 | 0.11€
BH1750 (To be added by your-self after manufacturing) |  | SEN0097 (DFRobot) |  | 1 | 4.15€
PCB manufacturing |  |  |  | 1 | 2.00€
PCB Assembly considering Extended components |  |  |  | 1 | 11.31€
 |  |  |  | Total IR Light | 23.57€
Back Pannel Socket
Comment | Designator | Footprint | JLCPCB Part # | Quantity | Price Ex Vat
Connector | I2C,PCOOL0,PCOOL1,PCOOL2,PCOOL3 | 640456-4 | C86504 | 5 | 0.52€
Connector | DHT1,DHT2,DHT3 | 640456-3 | C86503 | 3 | 0.31€
Connector | NTC0,NTC1,NTC2,NTC3,NTC4 | 640456-2 | C86502 | 5 | 0.52€
PCB manufacturing |  |  |  | 1 | 2.00€
PCB Assembly considering Extended components |  |  |  | 1 | 4.00€
 |  |  |  | Total BP Socket | 7.35€
Extra components for outdoor experiments
Comment | Description | Footprint |  | Quantity | Price Ex Vat
Flat NTCs | Flat Kapton NTCs 10 kΩ | 103JT-025 |  | 10 | 4.10€
Oled Screen | Display 128 x 64pixels | MDOB128064WV-YBI |  | 1 | 11.50€
Arduino MEGA | Dev. Board MEGA 2560 Rev3 | A000067 |  | 1 | 43.60€
Heat Resistor | 100 Ohms 10W | THS10100RJ |  | 4 | 10.64€
DHT22 | SENSOR HUMID/TEMP 5V DTL 2% MOD | SEN-10167 |  | 1 (max 3) | 9.20€
Enclouse 3D printed |  |  |  | 1 | 50€
 |  |  |  | Total extra components | 129.04€
 |  |  |  | Total | 217.16€

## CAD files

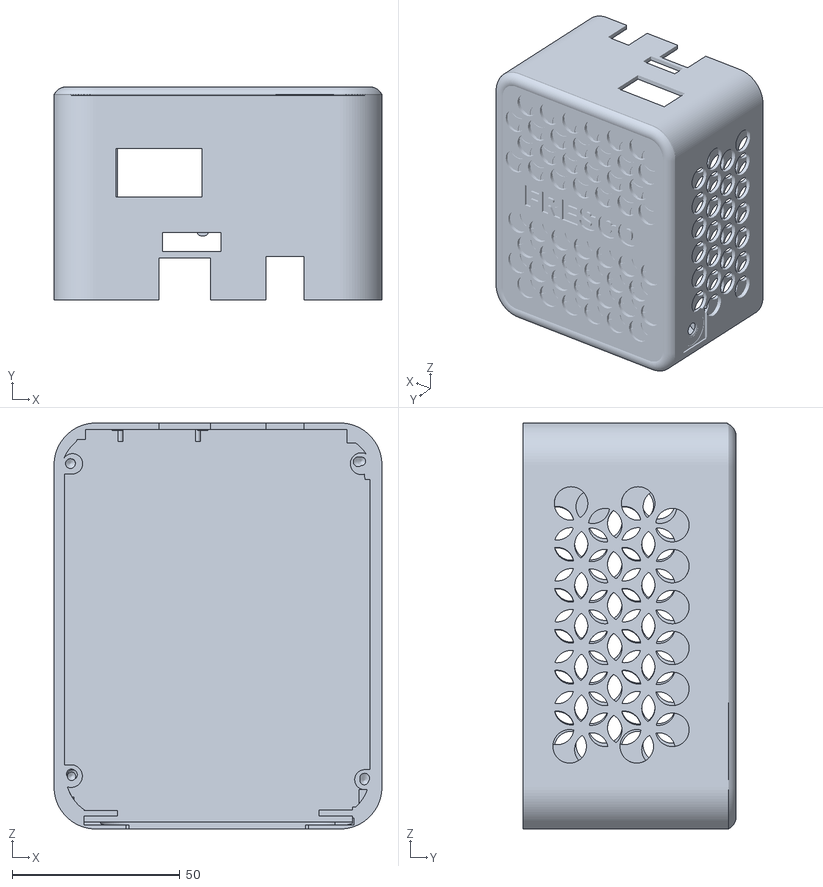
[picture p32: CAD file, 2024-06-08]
3D_enclosure/Main_body_FRESCO.stl
97.7 x 63.6 x 121.0

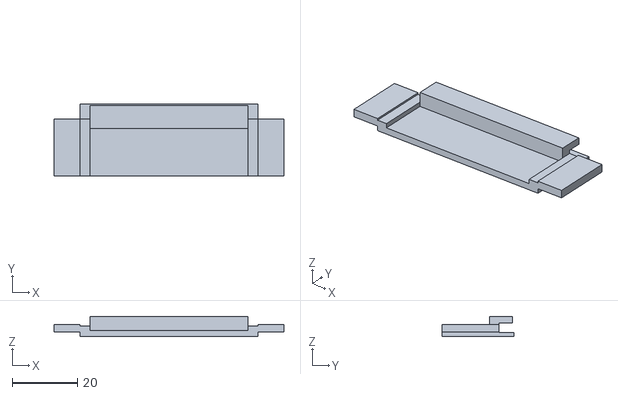
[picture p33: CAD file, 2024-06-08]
3D_enclosure/back_panel_FRESCO.stl
70.4 x 22.1 x 6.23

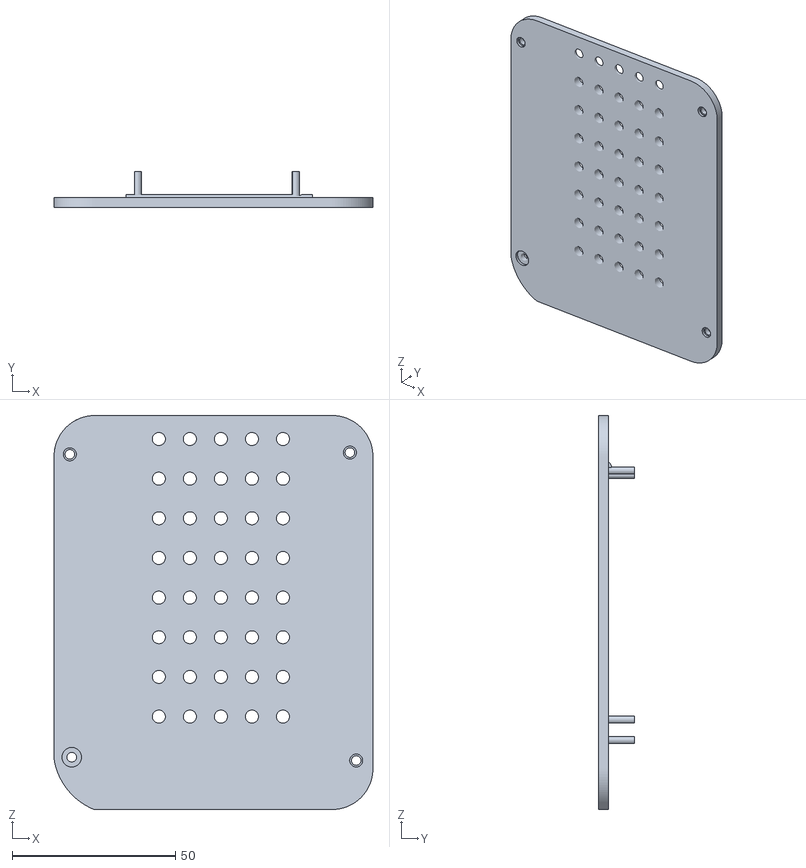
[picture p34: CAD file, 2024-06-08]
3D_enclosure/Base_FRESCO.stl
97.7 x 11.0 x 120.7

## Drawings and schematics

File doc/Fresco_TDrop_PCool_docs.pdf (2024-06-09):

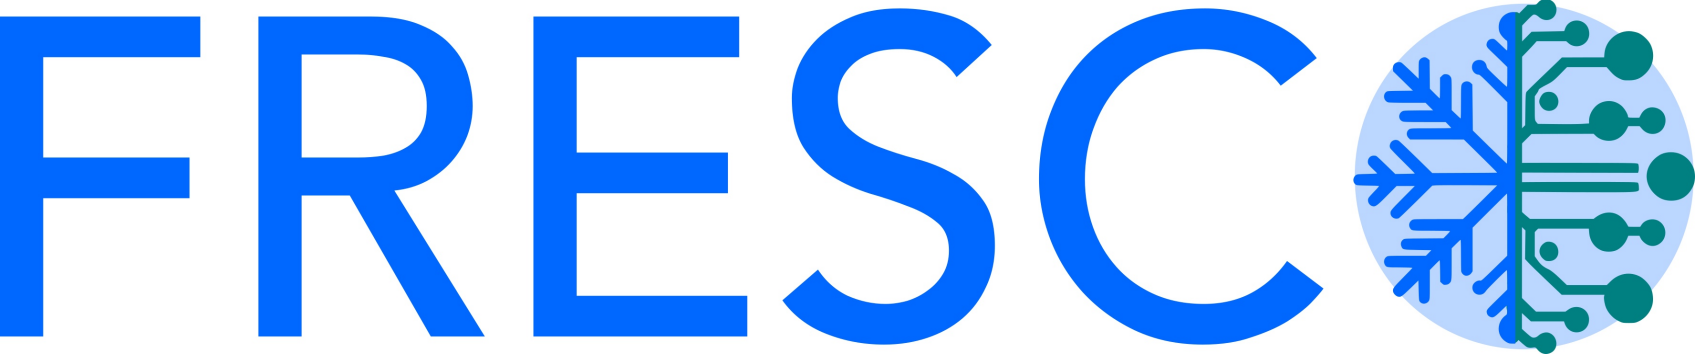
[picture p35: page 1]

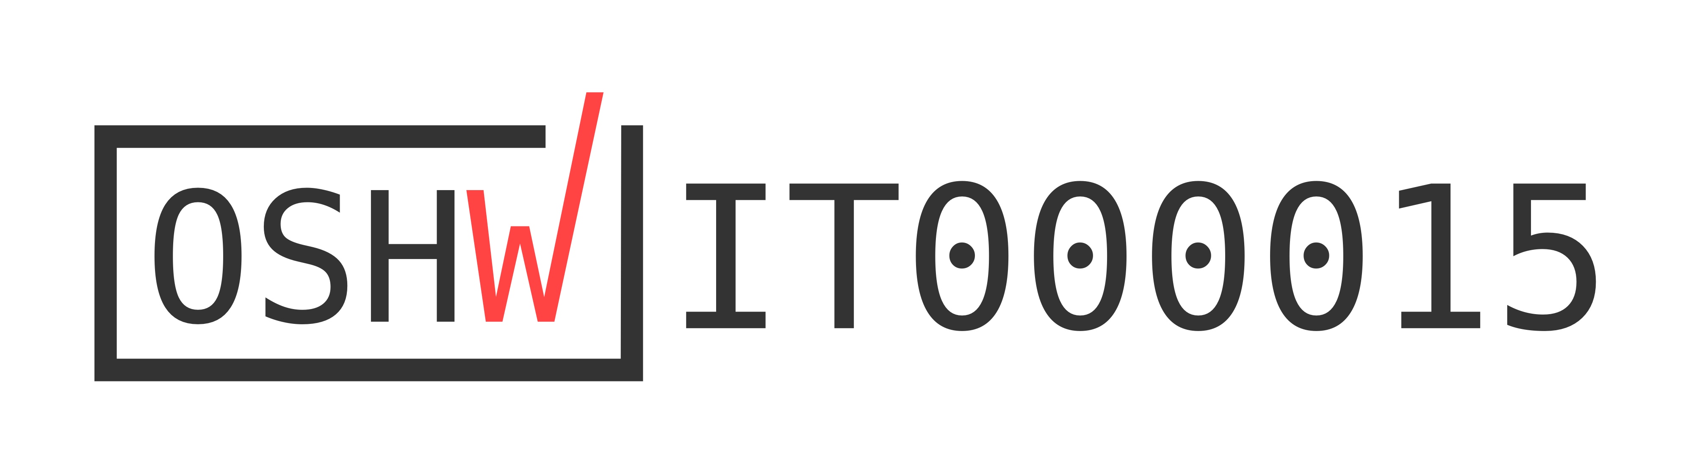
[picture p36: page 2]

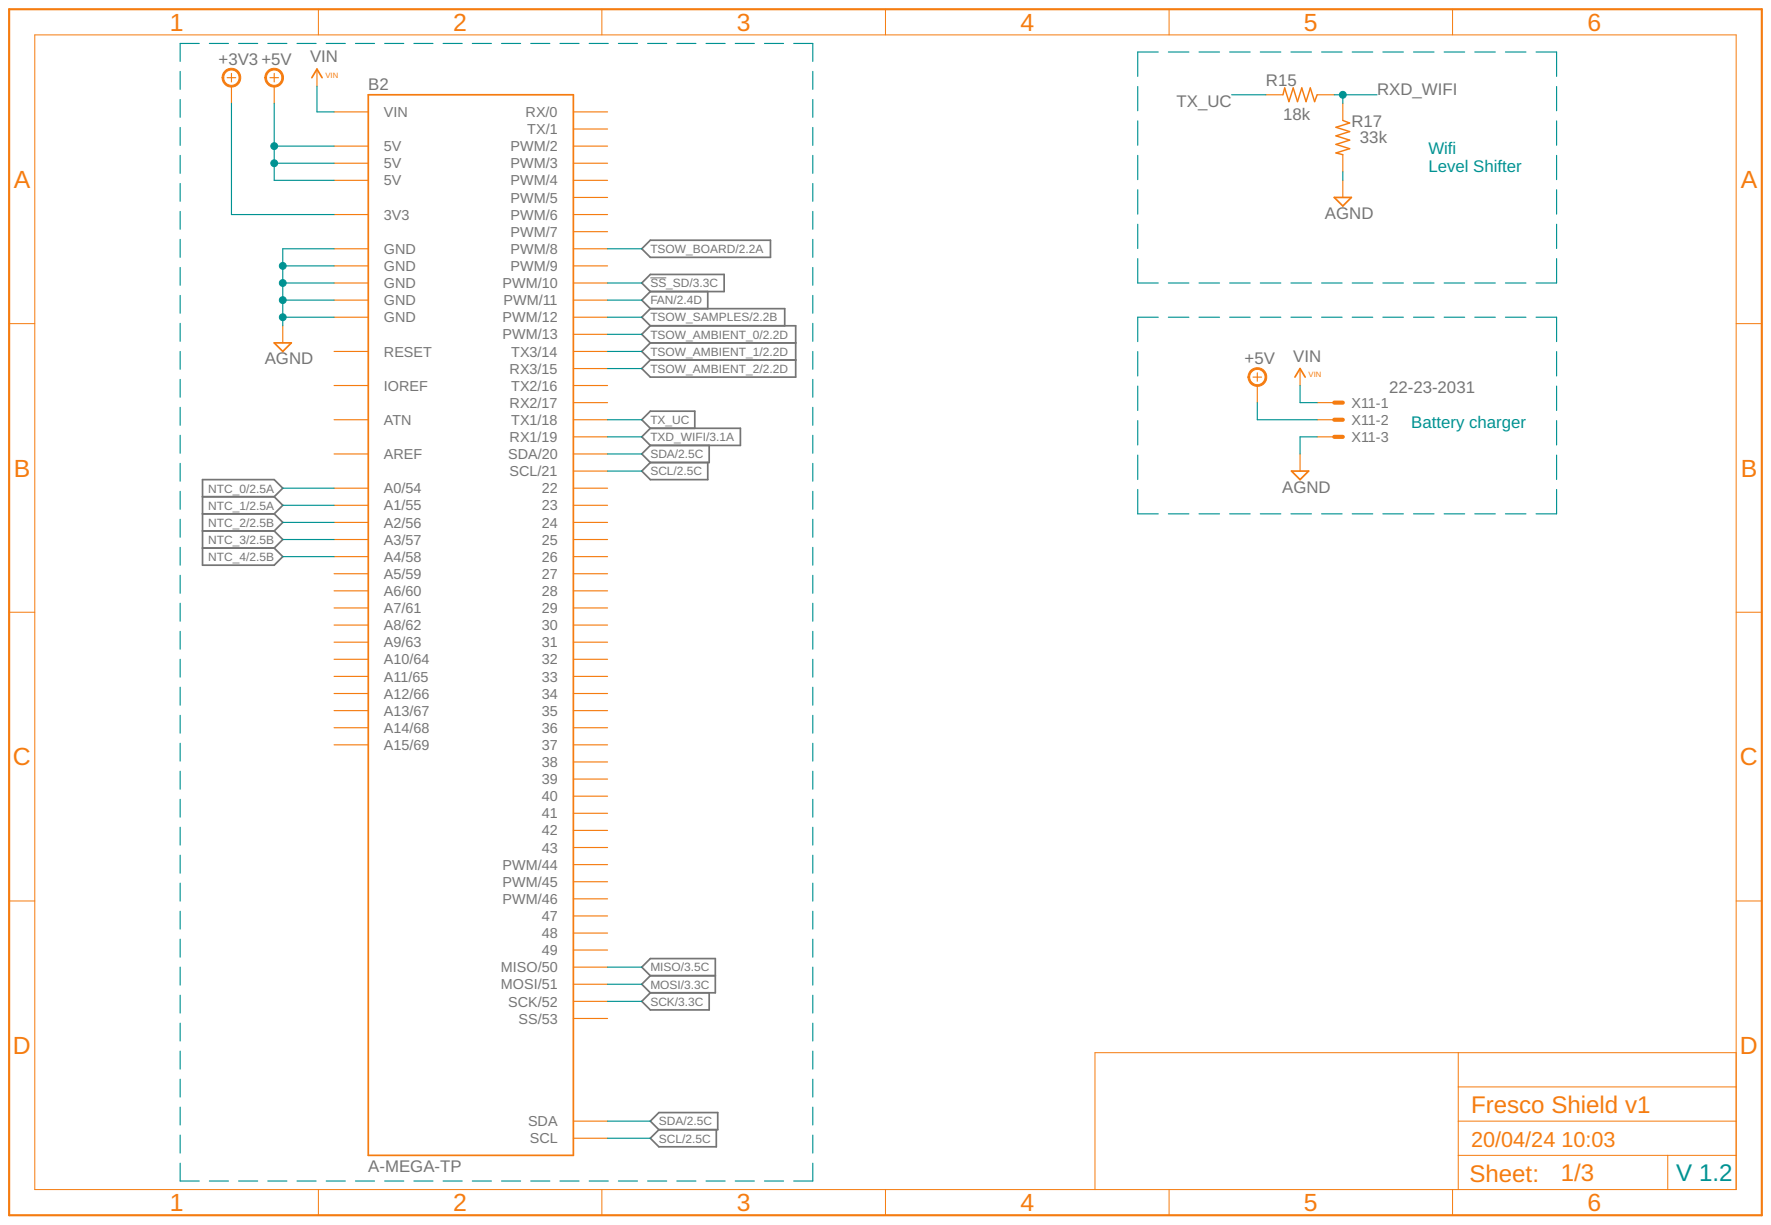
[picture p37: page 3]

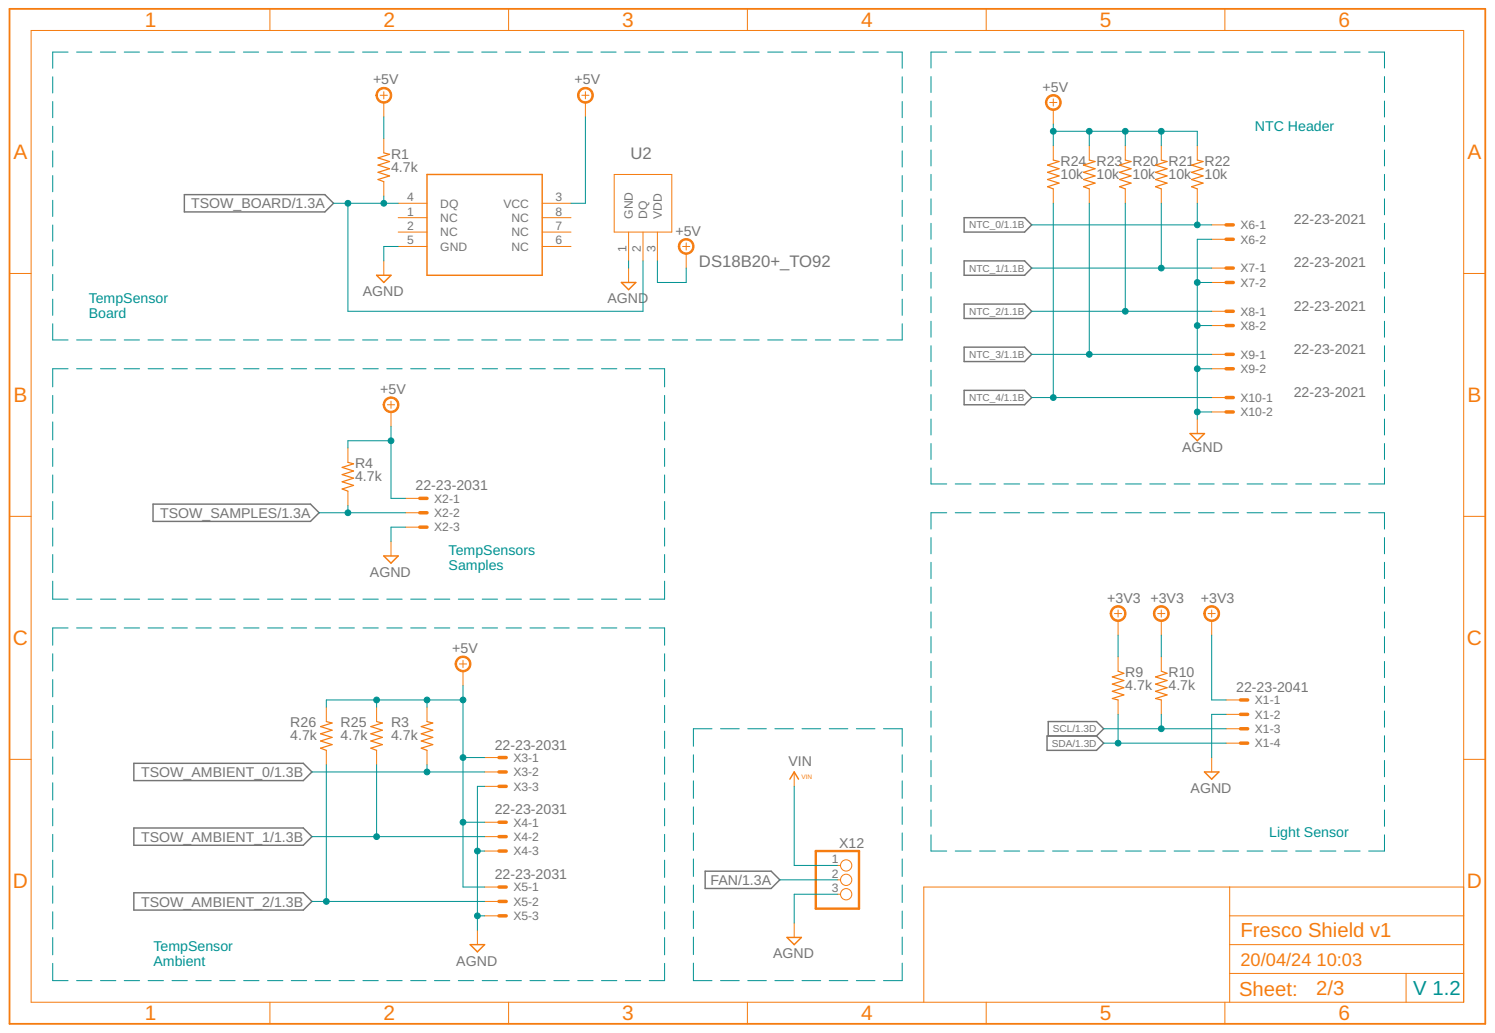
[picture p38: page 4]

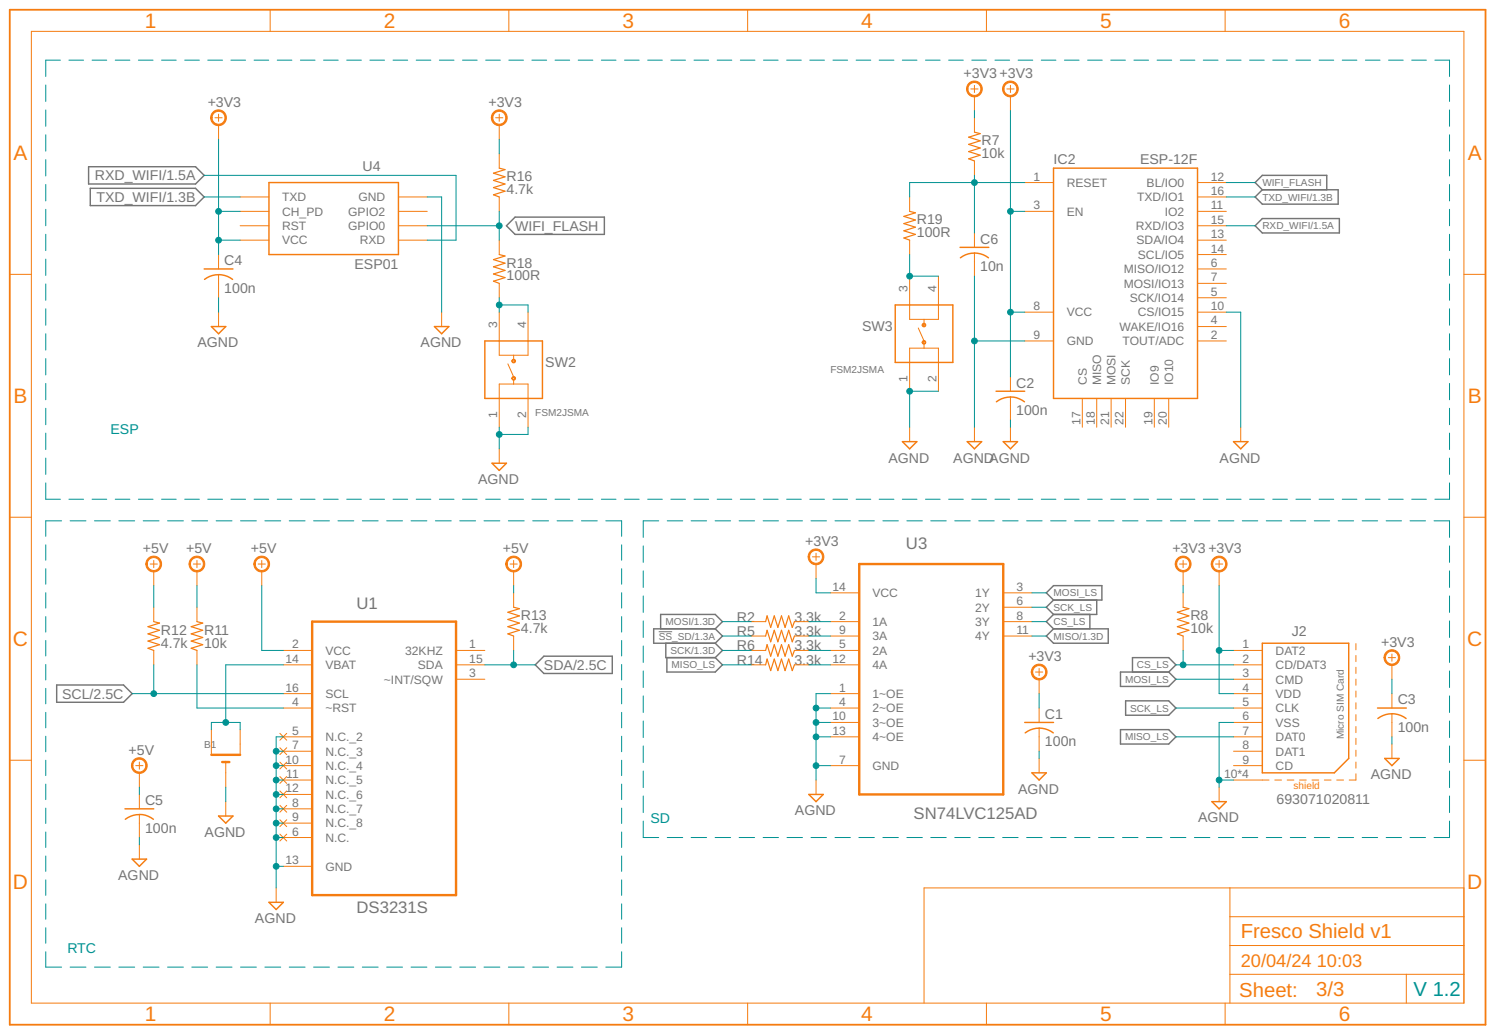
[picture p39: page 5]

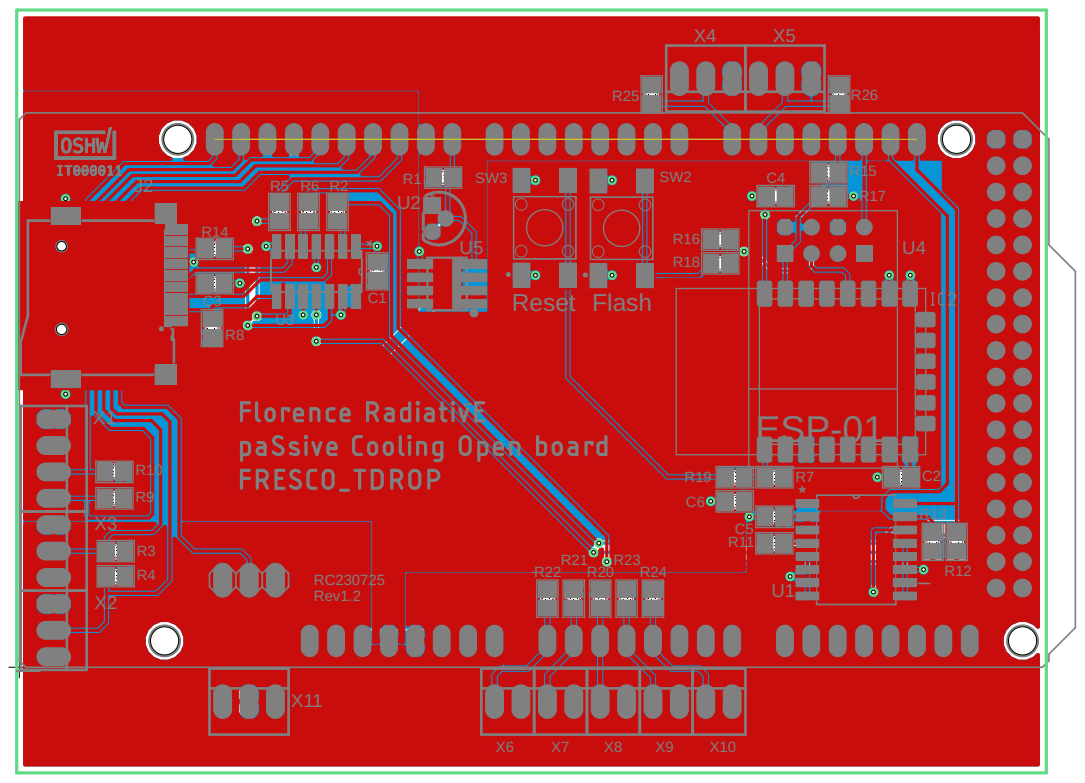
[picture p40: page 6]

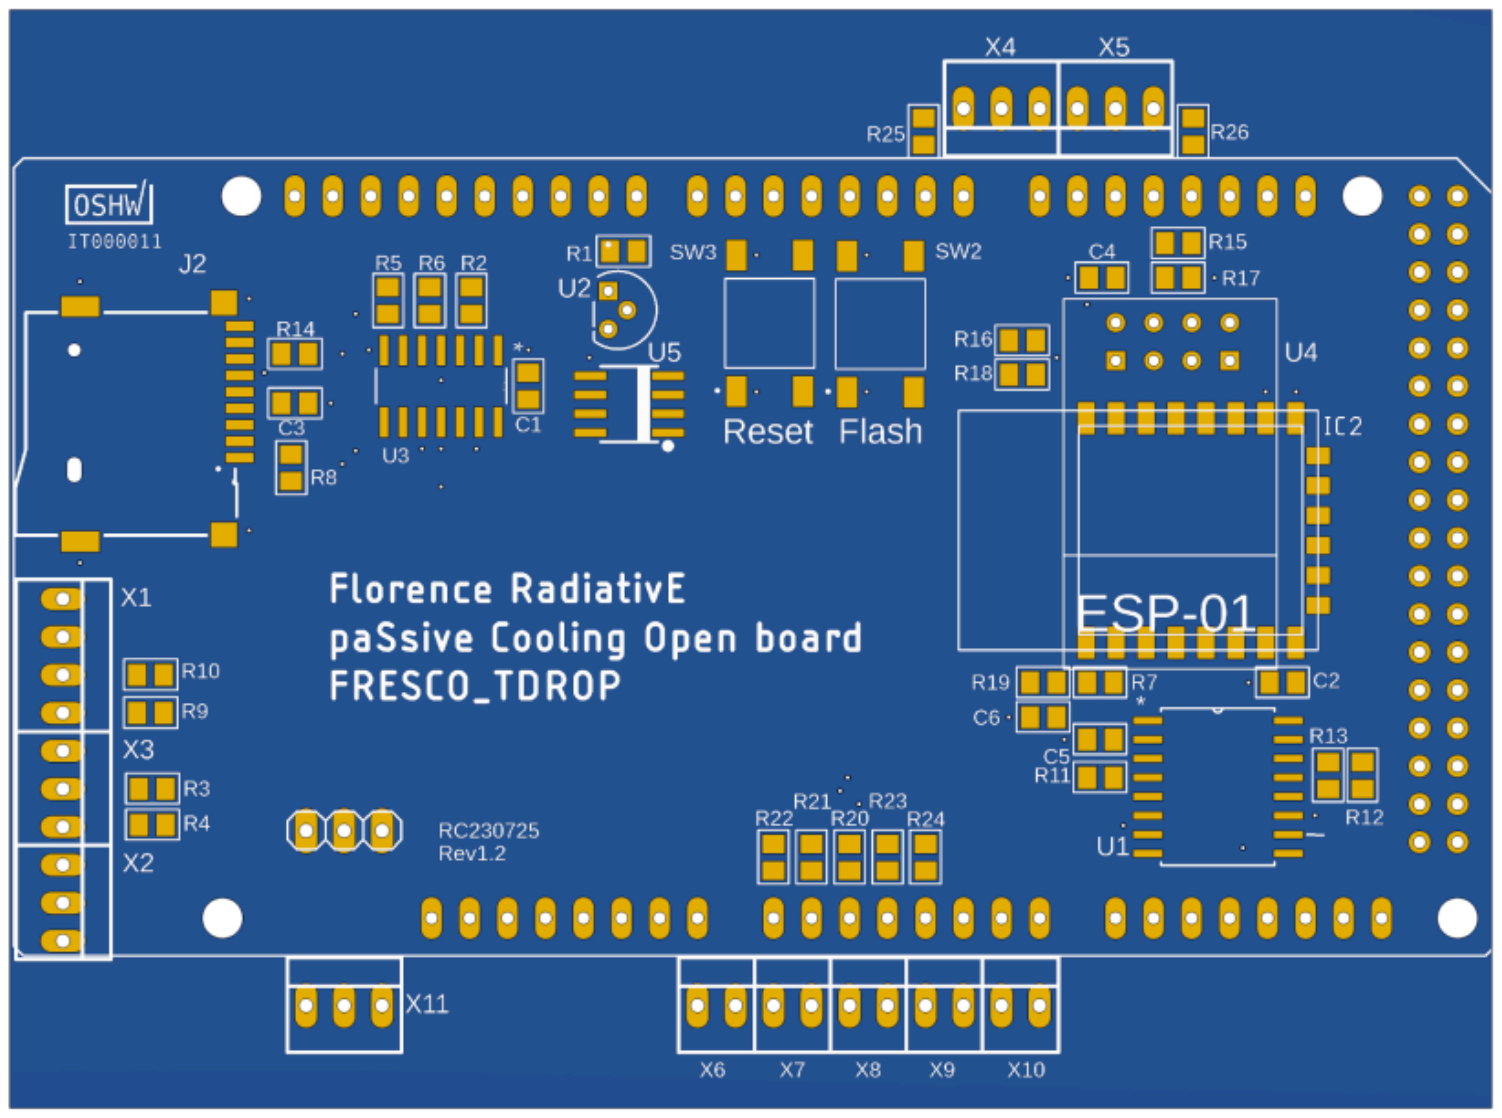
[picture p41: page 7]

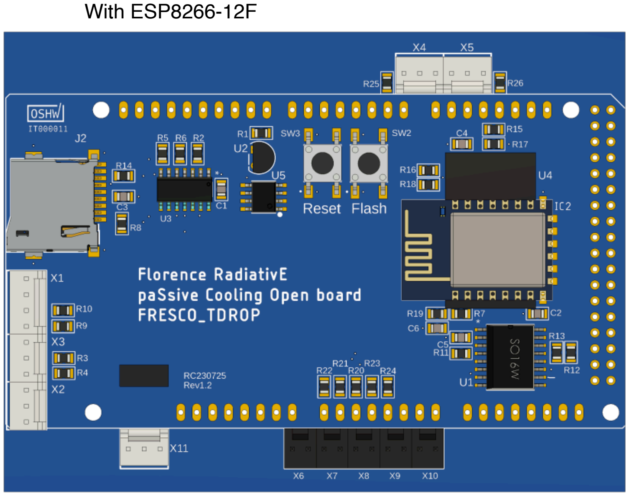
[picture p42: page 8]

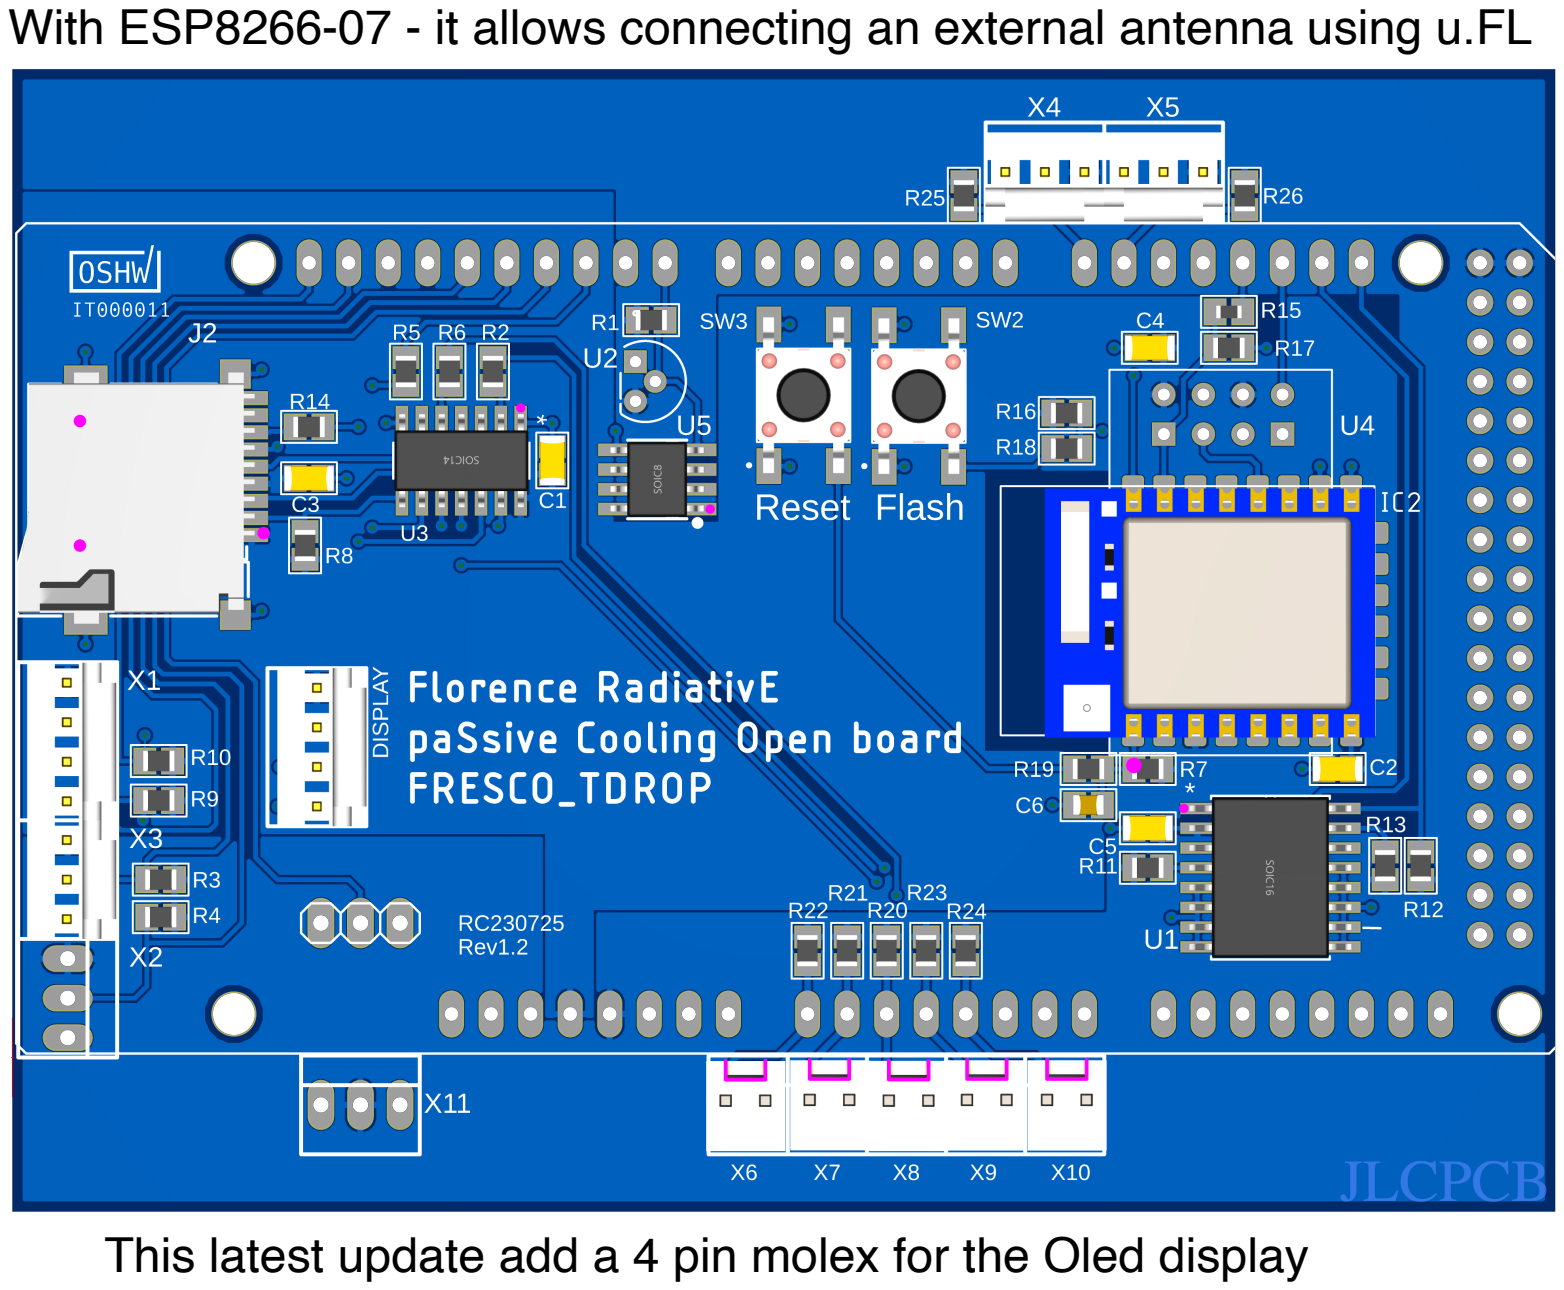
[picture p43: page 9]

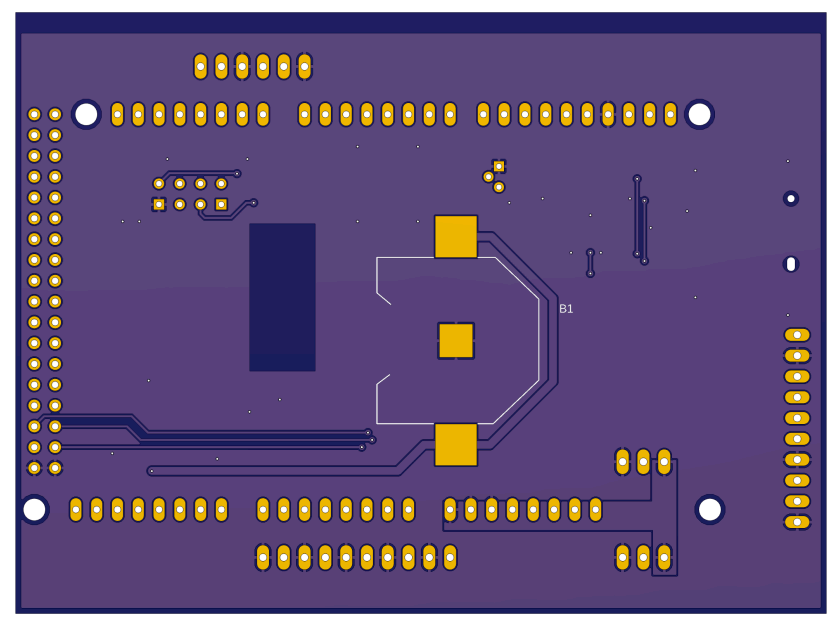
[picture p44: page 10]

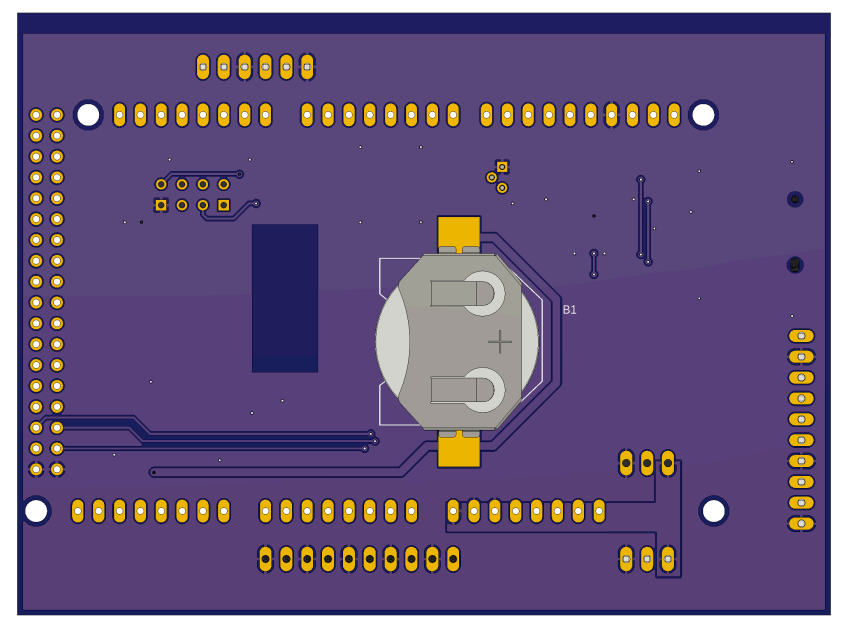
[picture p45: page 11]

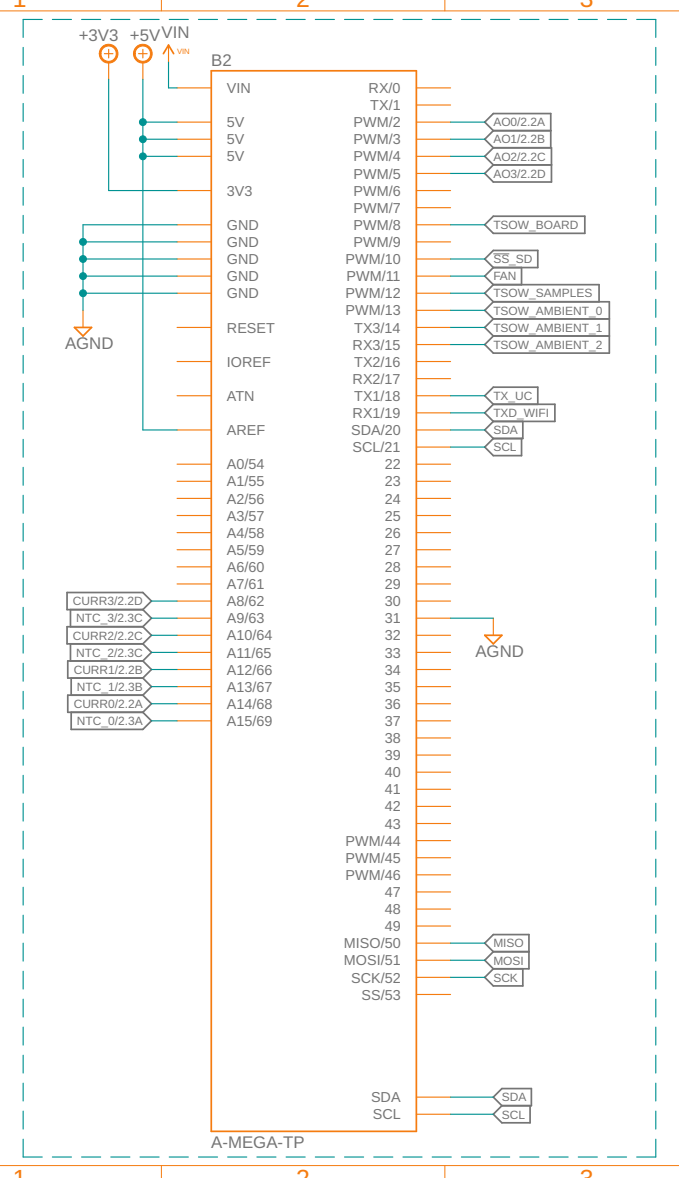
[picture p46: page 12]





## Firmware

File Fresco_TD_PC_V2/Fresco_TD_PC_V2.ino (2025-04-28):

/* PCool Includes */
#include <PID_v1_rc.h>
#include <arduino-timer.h>
/* Tdrop Includes */
#include <OneWire.h>
#include <DallasTemperature.h>
#include <DHT.h>
#include <BH1750.h>
#include <Wire.h>
#include <SPI.h>
#include <Adafruit_MLX90614.h>
#include <RTClib.h>
#include <U8glib.h>
#include <SD.h>
#include <string.h>

#define __STARTUP_MESSAGE_ENABLED__

#define __SEND_CURRENT__
#define __SEND_POWER_DENSITY__

/* Firmware Version */
#define __FW_MAJVERSION__ 3
#define __FW_MINVERSION__ 0
//#define __FW_BUILDVERSION__     0       // if not equal to 0 (zero) EEPROM is reset to default values
#define __FW_AUTHOR__ "RConcas, JWerlé and GELio"

#define PCOOL_GET_TEMPERATURE_TIMER 10000  // 10 ms
#define PCOOL_PIDOUT 1000000               // 1 s

#define PCOOL_GET_CURRENT_TIMER 10000        // 10 ms
#define PCOOL_AVERAGE_CURRENT_TIMER 1000000  // 1 s
#define delayms 1
#define PID_SAMPLE_TIME 100  // 200ms

#define ANALOG_CHANNELS 4

/* Analog FrontEnd parameters */
#define R_SHUNT 1
#define R_LOAD 100
#define PSUPPLY_VOLTAGE 12 //Update this value after measuring the voltage across the heater resistor and adjust the PID parameters accordingly
#define R_AMPLI 39
const float Sample_Surface_Default = 0.0036;
float SAMPLE_SURFACE;

/* Analog pins */
#define PIN_NTC0 A15
#define PIN_CURR0 A14
#define PIN_NTC1 A13
#define PIN_CURR1 A12
#define PIN_NTC2 A11
#define PIN_CURR2 A10
#define PIN_NTC3 A9
#define PIN_CURR3 A8

#define PIN_PWM0 2
#define PIN_PWM1 3
#define PIN_PWM2 4
#define PIN_PWM3 5

#define PIN_NTC_TDROP0 A0
#define PIN_NTC_TDROP1 A1
#define PIN_NTC_TDROP2 A2
#define PIN_NTC_TDROP3 A3
#define PIN_NTC_TDROP4 A4

/* PID */
#define PID_PARAMETER_GET_CHAR "?"
#define PID_PARAMETER_GET_VALUE -2

/*DEFINITION*/
#define DHTPIN 13
#define DHTPIN2 14
#define DHTPIN3 15
#define ONE_WIRE_BUS2 8 /* Sensor on board*/ /*Remember to not put it in the parallel line of the sensors that go in the external box*/
#define DHTTYPE DHT22                        // DHT 22  (AM2302)
#define esp8266 Serial1                      //RX and TX set on Serial1 --> RX2 and TX2 of Arduino Mega
/*NTC parameters*/
#define RT0 10000  // Ω
#define VCC 5      //Operating Voltage
#define R 10000    //R=10KΩ Pull Up resistor
#define T0 298.15
#define B_default 3380  //  B NTC default
int B = 3380;           //  K NTC part number NXFT15XH103FA2B100 or 3455
#define irrcal_default 3.4
/*Task times */
//#define RESET_TIME 14400000 //time for reset function every 4 hours in milliseconds -- 7200000 (2 hours)
//unsigned long ResetTime = RESET_TIME;
//#define TASK1 3000                  //gettemp
#define TASK1_default 1000
#define TASK2_default 2000
#define TASK3_default 3000
#define TASK4_default 10000
unsigned int TASK0 = 10;   	//gettemp fast reading before move mean
unsigned int TASK1 = 1000;	//gettemp average
unsigned int TASK2 = 2000;  //gettemp
unsigned int TASK3 = 3000;	// display
unsigned int TASK4 = 10000;  //Log data and send them using string


static uint8_t displayState = 0;
int pidvalue = 0;
double newsetpoint = 0;
/* Pid command structure */
typedef struct _pidCommand {
  String parameter;
  uint8_t channel;
  float value;
} pidCommand;

/* DDS command structure */
typedef struct _pidParameters {
  double PidSetpoint;
  double PidInput;   // ok
  double PidOutput;  // ok
  double Kp;         // ok
  double Ki;         // ok
  double Kd;         // ok
} pidParameters;

/* PID */
double PidSetpoint = 0;
double PidInput[ANALOG_CHANNELS] = { 0, 0, 0, 0 };
double PidOutput[ANALOG_CHANNELS] = { 0, 0, 0, 0 };
double Kp[ANALOG_CHANNELS] = { 200, 0, 0, 200 };  // Here the Proportional Gain PID parameter to be adjusted
double Ki[ANALOG_CHANNELS] = { 0, 0, 0, 0 };      // Here the Integral Gain PID parameter to be adjusted
double Kd[ANALOG_CHANNELS] = { 0, 0, 0, 0 };      // Here the Derivate Gain PID parameter to be adjusted

pidParameters heaterControllerParameters[ANALOG_CHANNELS];

PID heaterController[ANALOG_CHANNELS] = {
  PID(&PidInput[0], &PidOutput[0], &PidSetpoint, Kp[0], Ki[0], Kd[0], DIRECT),
  PID(&PidInput[1], &PidOutput[1], &PidSetpoint, Kp[1], Ki[1], Kd[1], DIRECT),
  PID(&PidInput[2], &PidOutput[2], &PidSetpoint, Kp[2], Ki[2], Kd[2], DIRECT),
  PID(&PidInput[3], &PidOutput[3], &PidSetpoint, Kp[3], Ki[3], Kd[3], DIRECT)
};


/*---------*/
double currentCalibration = 1000 * PSUPPLY_VOLTAGE * R_SHUNT / (R_SHUNT + R_LOAD); // tension at R_SHUNT
//double POWER_DENSITY_FACTOR = 1000 * (float)PSUPPLY_VOLTAGE * (R_LOAD / (R_SHUNT + R_LOAD)) / SAMPLE_SURFACE;
int count = 0;
long temperatureCounter = 0;
long temperatureCounterNTC = 0;
long currentCounter = 0;
double Imax_R_LOAD = PSUPPLY_VOLTAGE * R_LOAD / (R_SHUNT + R_LOAD); // max current initialization* R_LOAD
double currentValue[ANALOG_CHANNELS] = { 0, 0, 0, 0 };
double currentCalibrationValue[ANALOG_CHANNELS] = { 0, 0, 0, 0 };
double powerDensity[ANALOG_CHANNELS] = { 0, 0, 0, 0 };
double temperatureValue[ANALOG_CHANNELS] = { 0, 0, 0, 0 };
double averageTemperatureValue[ANALOG_CHANNELS] = { 0, 0, 0, 0 };
double heaterValue[ANALOG_CHANNELS] = { 0, 0, 0, 0 };

const uint8_t currentSensingPin[ANALOG_CHANNELS] = { PIN_CURR0, PIN_CURR1, PIN_CURR2, PIN_CURR3 };
const uint8_t temperatureSensingPin[ANALOG_CHANNELS] = { PIN_NTC0, PIN_NTC1, PIN_NTC2, PIN_NTC3 };
const uint8_t heaterPin[ANALOG_CHANNELS] = { PIN_PWM0, PIN_PWM1, PIN_PWM2, PIN_PWM3 };

/*Timer definition*/
Timer<5> timer;                                                   // create a timer with N tasks and microsecond resolution
Timer<4, micros> timerPcool;  // create a timer with 1 task and microsecond resolution

String receivedString = "";   // a String to hold incoming data
bool stringComplete = false;  // whether the string is complete

/* Function prototypes */
bool GetTemperature(void *);
bool GetCurrent(void *);
bool SendResults(void *);

U8GLIB_SSD1306_128X64 u8g(U8G_I2C_OPT_NONE | U8G_I2C_OPT_DEV_0);  // I2C / TWI

float tempBoard = 0;  //The sensor used to measure the temp. on Board
float t, h, t2, h2, t3, h3, irr, IR_temp_amb, IR_temp_sky = 0;
int irr_cal = 3.4;
/**/
String str;
String str0;
String clock_status;
String Date_Time;
String sd_status;
String wifi_status;
String Date;
String Time;
String apIP;
String localIP;

/* Temperature Sensors  */
DHT dht(DHTPIN, DHTTYPE);
DHT dht2(DHTPIN2, DHTTYPE);
DHT dht3(DHTPIN3, DHTTYPE);

/* On board using DS18B20 */
OneWire oneWireBoard(ONE_WIRE_BUS2);
DallasTemperature sensorsBoard(&oneWireBoard);

/* LIGHT Sensor */
BH1750 lightMeter;
/* IR Sensor for Ambient and Sky temperature */
Adafruit_MLX90614 mlx = Adafruit_MLX90614();
/* SD CARD */
const int chipSelect = 10;  // Pin used for SD module (Do not change it! it is defined on the PCB board)
File myFile;                // Create a file to store the data
/* Real Time Clock */
RTC_DS3231 rtc;  //RTC

int progress = 0;
const int shieldPin = 31;         // Digital pin connected to the shield
bool shieldPresent;               // Global variable
bool parametersReceived = false;  // Flag to indicate whether parameters have been received

unsigned long startTime = 0;
unsigned long interval = 0;
const unsigned long displayInterval = 2000;  // Adjust the interval as needed

const int numChannels = 5;
const int numOtherSensors = 10;
int analogPins[numChannels] = { A0, A1, A2, A3, A4 };
const uint8_t temperatureSensingPinNTC[numChannels] = { PIN_NTC_TDROP0, PIN_NTC_TDROP1, PIN_NTC_TDROP2, PIN_NTC_TDROP3, PIN_NTC_TDROP4 };

double averageTemperatureNTCValue[numChannels] = {0, 0, 0, 0 ,0}; // create list to contain avg NTC temp
double temperatureValueNTC[numChannels] = { 0, 0, 0, 0, 0 };      // create list to contain NTC temp
float VRT[numChannels];
float VR[numChannels];
float RT[numChannels];
float ln[numChannels];
float T[numChannels];

/*--- SETUP ---*/
void setup() {
  receivedString.reserve(100);  // reserve 100 bytes for the receivedString
  Serial.begin(115200);         // initialize serial communication at 57600 bits per second:
  esp8266.begin(115200);
  /**/
  /*TDrop First, it is always mounted*/
  pinMode(shieldPin, INPUT_PULLUP);
  bool shieldPresent = digitalRead(shieldPin) == LOW;
  /**/
  if (shieldPresent) {
    Serial.println("SHIELD_PRESENT");
    initializePCool();
  } else {
    Serial.println("SHIELD_NOT_PRESENT");
  }
  Tdropstartup(shieldPresent);

#ifdef __STARTUP_MESSAGE_ENABLED__
  Serial.print("PCool");
  Serial.print(" v");
  Serial.print(__FW_MAJVERSION__);
  Serial.print(".");
  Serial.print(__FW_MINVERSION__);
  Serial.print("-");
  Serial.println(__FW_AUTHOR__);
  Serial.print(__DATE__);
  Serial.print(" ");
  Serial.println(__TIME__);
#endif
}

/*--- LOOP ---*/
void loop() {
  pidCommand command;
  if (stringComplete) {
    receivedString = "";  // clear the string
    stringComplete = false;
  }
  bool shieldPresent = digitalRead(shieldPin) == LOW;
  if (shieldPresent) {
    if (heaterController[0].Compute()) analogWrite(heaterPin[0], PidOutput[0]);
    if (heaterController[3].Compute()) analogWrite(heaterPin[3], PidOutput[3]);
  }

  timer.tick();
  timerPcool.tick();

  if (esp8266.available() > 0) {
    String command = esp8266.readStringUntil('\n');
    if (command == "RestartArduino") {
      // Restart the Arduino
      asm volatile("  jmp 0");
    }
  }
}

void Tdropstartup(bool shieldPresent) {
  moduledraw(shieldPresent);
  setParametersFromESPWithProgressBar();      // Initialize ESP8266 parameters
  Sensors_initialization();                   // Initialize sensors
  RTC_initialization();                       // Initialize RTC
  SD_initialization(shieldPresent);           // Initialize SD card
  setWiFiParametersFromESPWithProgressBar();  // Wait and read WiFi status
  init_screen();                              // Initialize screen
  /* Timer setup */
  /*TDrop*/
  // Measurement of NTC temp
  timer.every(TASK0,SetTemperatureNTC, &shieldPresent);
  // To know date and time
  timer.every(TASK1, SendTemperatureNTC);
  timer.every(TASK2, datalog, &shieldPresent);
  timer.every(TASK3, displaying_data, &shieldPresent);
  timer.every(TASK4, SendDataToESP8266, &shieldPresent);
  //timer.every(ResetTime, resetFunc);
}

// void getstring() {
//   esp8266.println(str);  //the string containing the data is sent to the ESP for the web and dashboard
// }

/*PCool initializaion, it is used if the module is loaded otherwise it is ignored*/
void initializePCool() {
  /* PID Setup */
  heaterController[0].SetSampleTime(PID_SAMPLE_TIME);
  heaterController[3].SetSampleTime(PID_SAMPLE_TIME);
  heaterController[0].SetMode(AUTOMATIC);  // Turn the PID on
  heaterController[3].SetMode(AUTOMATIC);  // Turn the PID on
  // PidSetpoint = 22.0;
  /* Current Setup */
  CurrentCalibration();
  analogReference(EXTERNAL);
  /* Timer setup */
  // Set up periodic tasks for PCool module
  timerPcool.every(PCOOL_GET_TEMPERATURE_TIMER, SetTemperature);
  timerPcool.every(PCOOL_GET_CURRENT_TIMER, GetCurrent);
  timerPcool.every(PCOOL_PIDOUT, SendTemperature);
  timerPcool.every(PCOOL_AVERAGE_CURRENT_TIMER, SendCurrent);
}

/* Timer Callback functions */

bool SetTemperature(void *) {
  //bool *shieldPresent = (bool *)param;
  SetTemperatureChannel(0);
  SetTemperatureChannel(3);
  temperatureCounter++;
  return true;
}

bool SetTemperatureNTC(void *) {
  //bool *shieldPresent = (bool *)param;
  SetTemperatureChannelNTC(0);
  SetTemperatureChannelNTC(1);
  SetTemperatureChannelNTC(2);
  SetTemperatureChannelNTC(3);
  SetTemperatureChannelNTC(4);

  temperatureCounterNTC++;
  return true;
}

bool SendTemperatureNTC(void *) {
  //  bool *shieldPresent = (bool *)param;
  SendTemperatureChannelNTC(0);
  SendTemperatureChannelNTC(1);
  SendTemperatureChannelNTC(2);
  SendTemperatureChannelNTC(3);
  SendTemperatureChannelNTC(4);
  temperatureCounterNTC = 0;
  return true;
}
bool SendTemperature(void *) {
  //bool *shieldPresent = (bool *)param;
  SendTemperatureChannel(0);
  SendTemperatureChannel(3);
  temperatureCounter = 0;
  return true;
}
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

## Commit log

2024-01-21 Add files via upload
    This is the code made for the ESP8266. It receives the string passed by the arduino board and sent it to an internal webpage managed by littleFS and also through the influxdb making a local database 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
    The code allows sending on the local server different events# that are used to manage the data and to show them in charts.
2024-04-09 FRESCO Board startup_Software
2024-04-09 Update for ESP8266 sync NTP Date and Time
    The updated firmware allows sync the Date and Time using NTP and then transfer it to Arduino for RTC update and setting
2024-04-20 Documentation about FRESCO
    The file contains the FRESCO TDrop and PCool documentation about schematics, PCB and 3D rendering of each shield
2024-04-20 FRESCO_I/O_desc
    A short description about the Input and Output Pin available on the FRESCO board. It provides some specification about the pin if they are digital or analog, how they are named inside the firmware an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
2024-04-21 Rename FRESCO Board startup_Software.pdf to doc/FRESCO Board startup_Software.pdf
2024-04-21 Schematic FRESCO's workflow
    a schematic representation about the workflow among arduino, ESP8266 and the local or cloud server exploiting InfluxDB V2 database and Grafana for the Dashboard
2024-04-23 Latest version of the Arduino
    The new firmware for Arduino Mega 2560 includes Tdrop and PCool controls.
2024-05-04 This is an example of Google Colab to track data collected with FRESCO and get immediate feedback on your Passive Radiative Cooling samples.
2024-05-05 This is an updated version of Google Colab to track data collected with FRESCO and display weather informations such as humidity, solar irradiance, Sky temperature, the sample and ambient temperature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
2024-05-05 This is an updated version of Google Colab to track data collected with FRESCO and display weather informations such as humidity, solar irradiance, Sky temperature, the sample and ambient temperature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
2024-05-15 Update Fresco_TD_PC_V2.ino
    The following code version solve the following issues:
    1) reading the right values from PCool (temperatures)
    2) reading the right values from PCool (power densitites)
    Now also the external setting of the PidSetPoint using the Webapp has been fixed and testes
2024-05-15 Add files via upload
    The upload improve the web app management and include new functionalities according to the module that is loaded on the main board.
2024-05-18 Update Fresco_TD_PC_V2.ino
    the Draw_PCoolTemps has been updated including the set point temperature
2024-05-18 Update ESP_Fresco_and_WebApp.ino
    new setting values included, now it is possible to choose the right PID set point (t, t2, t3 or one of the other sensors )or a value for the PID directly chooses by the user
2024-05-19 Add files via upload
    new description about the FRESCO I/O ports and the procedure to set up the PID Set Point or a different value for the temperature settings
2024-05-19 Add files via upload
    New I/O description for the FRESCO board have been included. Now a full guide about PID set point as function of the already installed sensors or based on a desired temperature value are detailed.
2024-05-26 Update Fresco_TD_PC_V2.ino
    renamed a written variable about power density on the SD with its correct label PD2
2024-05-26 Update of Webapp guide
    The new guide includes some information about the use of settings in the web app and how to set some entries such as: NTP, TZ-INFO, B value, Send data transfer time, displaying time, saving time. If 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
2024-06-02 Geber LightSensor and IR sensor
2024-06-08 3D enclosure parts
    [Base_FRESCO.stl, Main_body_FRESCO.stl, back_panel_FRESCO.stl]
2024-06-09 update with the latest PCBs representations
2024-06-09 updated schematics, PCBs and renderings
2024-10-08 Updated file containing the used libraries
    The new libraries contain all the needed files to set up the FRESCO board
2024-10-13 uploaded version of the FRESCO I/O pin description
    uploaded version of the FRESCO I/O pin description
2024-12-03 All the BOM and CPL files
    All the BOM and CPL files for the two FRESCO shields (TDrop and PCool), the light and IR sensor and the back panel.
2025-03-20 Print NTC Beta value on LCD screen during setup
2025-04-16 Update libraries
    The new zip file contains all the libraries needed to compile FRESCO firmware, it includes libraries for Arduino and ESP.
2025-04-16 Bill of Materials
    Summarized BoM version of all the components needed for building FRESCO
    [BoM.xlsx]
2025-04-21 New revised version
    This new version removes the de-bug functions. The firmware has been tested on Arduino MEGA2560 Rev3 and on DFRduino Mega2560 (Flash memory 128Kb).
